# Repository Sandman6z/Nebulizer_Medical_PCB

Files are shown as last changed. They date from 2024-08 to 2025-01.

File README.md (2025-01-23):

## Medical Atomizer on ventilators

- MCU: STM32C031G6U6

- MCU change to: STM32G031G6U6
 ---

## 注意事项
- 由于硅胶垫圈的原因，雾化片震动效果可能不好，更换后，雾化率提升，故降低boost电路电压，R29降为270kΩ
- 经过软件工程师ADC采集数据情况，C18电容NC效果较好
- 保持C20 NC

## 医用雾化器-雾化专用芯片设计注意事项

- 三脚电感值，测试

- 供电输入5V不耐冲击，加TVS等防护
- 高压网络layout和器件封装，参考雾化片手册注意事项
- 雾化片功率检测方式

## 测试数据
### 2024.12.17
- 采样点电流：
  - 有水：133mV
  - 空杯：159mV
  - 无杯：78mV
- MOS电压：
  - 有水：72~90V
  - 空杯：68V
  - 无杯：212V（150V的TVS钳位到160V）

---
---

<!-- 板子背景，更改前的状态，遇到的问题，做的更改，当前设计简述 -->

## 背景信息

- **硬件设计**:
  - 使用Microchip公司的`PIC16F1578-I/SS`微控制器单元(MCU)。
  - 编程环境为`MPLAB X IDE v5.50`，使用`xc8` C语言编译器。
  - 硬件仿真器为`PICKit3`。
  - 通过输出PWM信号驱动MOS管来雾化药物。
  - 与呼吸机通过三根信号线进行通讯，包括使能信号`EN_Fog`、状态反馈信号`NebSt`和设备识别信号`Dev_NC`。

- **软件设计**:
  - 需要实现的功能包括与呼吸机的通信、状态反馈、扫频以确定最佳雾化频率、无水检测等。
  - 雾化器能够通过反馈信号告知呼吸机其工作状态。

## 更改前的状态

- 雾化器能够正常执行基本的雾化操作，但雾化率不理想[需由王工补充]
- 能够与呼吸机进行通信并反馈工作状态，但偶尔无法启动雾化功能
- 已经实现了扫频功能以确定最佳雾化频率，但扫频功能容易误识别

## 遇到的问题

1. **对于PI膜雾化片**:
   - 在剩余约0.5~1ml液体时会误判为无水状态，导致提前停机。
   - 这种误报警现象稳定出现，影响正常使用。

4. **不锈钢雾化片兼容性问题**:
   - 新的不锈钢雾化片与原有雾化片特性不同，需要重新调试扫频、水杯未连接、无水停机策略等来适应新雾化片。

3. **雾化片扫频不准**
   - 当前已经实现了扫频功能，但通过示波器查看扫频波形，若存在多个功率较大的频点时容易误识别，故而不工作在雾化片的最佳频点，需要更精确的电路。

4. **指示灯问题**:
   - 初始化时，工作指示灯的亮度不足，可能是软件控制的问题。

5. **LED状态问题**:
   - 当使能信号被取消后，LED会锁定在红色状态，无法回到初始化状态，除非重新启动雾化器。

这些问题需要进一步的软件优化和调试来解决，以确保雾化器的稳定运行和提高用户体验。

## 问题更改及改进

1. MCU
   - 原MCU为microchip的PIC16F1578-I/SS，IDE使用MPLAB X IDE，配置复杂，且软件通用性差，与公司生态不一致
   - 考虑到性能、价格、封装、生态等因素，将microchip MCU换成ST的STM32C031G6U6，价格近似，性能有质的提升，且外设满足所有功能，精度更高，封装尺寸小，更便于布局。与原厂FAE和各经销商确认过，供货长期且稳定，若量大价格可以更低
   - STM32C0系列与STM32G系列多种型号封装互相通用，后期若需要修改，也有更多选择，而无需修改PCB
   - 使用STM32CubeMX，使用图形化配置 + HAL库的方式，实现快速开发，满足易维护的要求

2. MOSFET
   - 原雾化电路驱动的LC电路可达到100V以上，但原NMOS耐压值不足，本次选择onsemi(安森美)家的FDN86246，耐压可达150V，Id 1.6A，均满足设计需求且余量充足
   - 封装更小，节省紧张的板空间

3. 扫频功能
   - 增加雾化驱动电路的电压和电流检测电路
   - 电压检测通过分压方式；电流检测通过检流电阻和运放电路的方式
   - 相较原简易电阻分压测电流方式，精度更高，且layout采用差分走线，避免layout造成的采样不准确的问题
   - 将电压和电流检测电路结合，配合软件逻辑，实现扫频功能。

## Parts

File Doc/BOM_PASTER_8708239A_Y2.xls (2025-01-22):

型号 | 封装 | 位号 | 元件编号
15nF±5%50VX7R | C0402 | C18,C21 | C114405
STM32G031G6U6 | QFN50P400X400X60-28N-D | U4 | C432210
510Ω±1%62.5mW | R0402 | R14,R15,R3,R4,R5,R6,R7,R8,R9 | C25123
30Ω±1%62.5mW | R0402 | R16 | C514796
1.25T-6P-WT | WAFER_1.25MMX6P_180 | J2 | C97377
1.25T-3P-WT | WAFER_1.25MMX3P_180 | J1 | C707315
100pF±5%100V | C0603 | C4 | C107033
1uF±10%25VX5R | C0402 | C1,C2 | C52923
SS24 | SMA-403D | SD1 | C50645
AO3410 | SOT23-3 | Q2 | C7524909
10uH/2.5A | SP0502 | L3 | C65664
1kΩ±0.1%62.5mW | R0402 | R33,R37 | C852624
330Ω±1%62.5mW | R0402 | R21,R32,R34 | C427237
220Ohm@100MHz | 0402-B | B1,B2,B4,B5,B6 | C85813
1K±25%@100MHz | 0805-B | B10,B3,B7 | C85835
10KΩ±1%62.5mW | R0402 | R28,R1,R13,R27 | C850723
4.7kΩ±1%62.5mW | R0402 | R11 | C400631
ME6211C33M5G-N | SOT95P270X145-5N | U2 | C82942
100nF±10%50VX7R | C0402 | C13 | C307331
0Ω±1%100mW | R0603 | R10,R30 | C21189
LED_BLUE | LED0603 | LED8,LED9,LED1,LED3,LED4,LED5,LED2 | C965807
10kΩ±1%62.5mW | R0402 | R20,R12,R25 | C25744
4.7kΩ±0.1%62.5mW | R0402 | R38,R35 | C728561
22uF±20%25V | C0805 | C10,C12,C8,C9,C11 | C45783
1Ω±1%500mW±100ppm/℃ | R1206 | R31 | C1882606
390kΩ±1%100mW | R0603 | R24,R26 | C23150
HSS1N20 | SOT95P237X122-3N | Q1 | C845589
TLV9051IDBVR | SOT23-5 | U1 | C1849429
47Ω±1%62.5mW | R0402 | R17,R19 | C427232
100nF±10%50VX7R | C0402 | C14,C15,C6,C16,C19 | C1525
AO3401 | SOT23 | Q3 | C727156
LED_GREEN | LED0603 | LED7 | C7371905
PESD5V2S2UT | SOT23 | ESD1,ESD2,ESD3 | C2827690
4.7uF±10%10VX5R | C0402 | C5 | C368809
LED_RED | LED0603 | LED6 | C965799
470uH±10%260mA | SP0502 | L2 | C167984
BZG03C150-M3-08 | DIOM5226X230N | TVS1 | C2761030
MT3608 | SOT95P280X110-6N | U3 | C84817
280kΩ±1%62.5mW | R0402 | R29 | C364982
NC | C0402 | ES10,ES11,ES9 | NC
22uH@100kHz/50V1812 | LINEFILTER | L1 | NC
NC | C0402 | C20 | NC
NC | JST_PH2.00-5 | J3 | NC

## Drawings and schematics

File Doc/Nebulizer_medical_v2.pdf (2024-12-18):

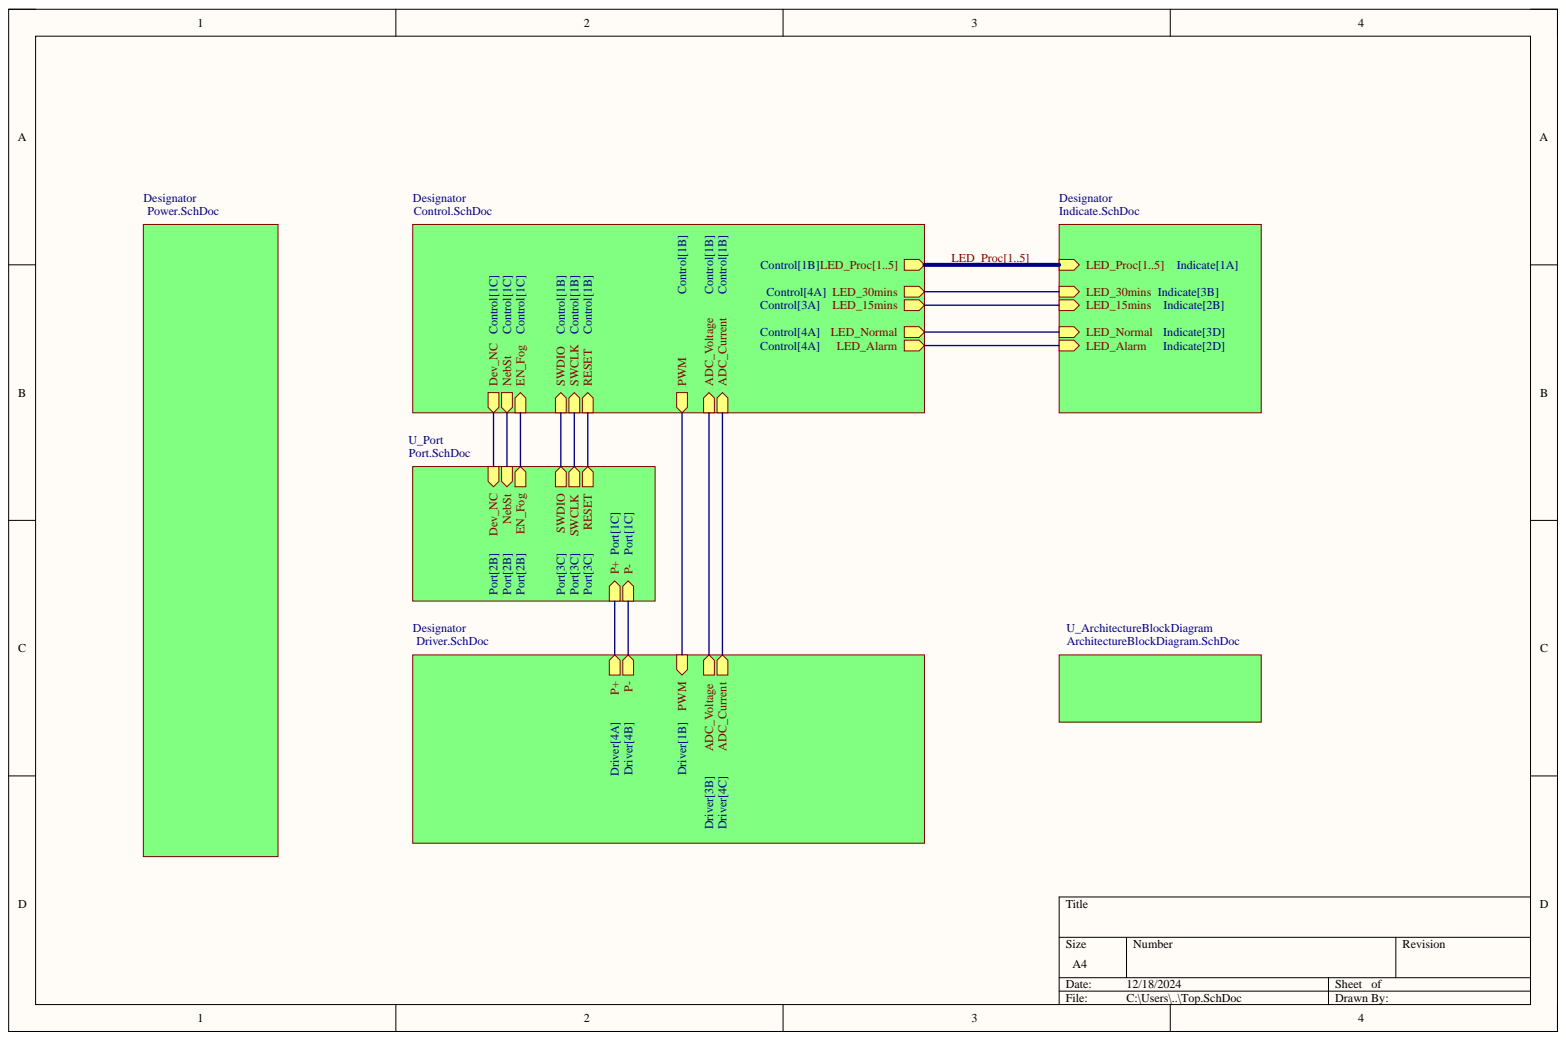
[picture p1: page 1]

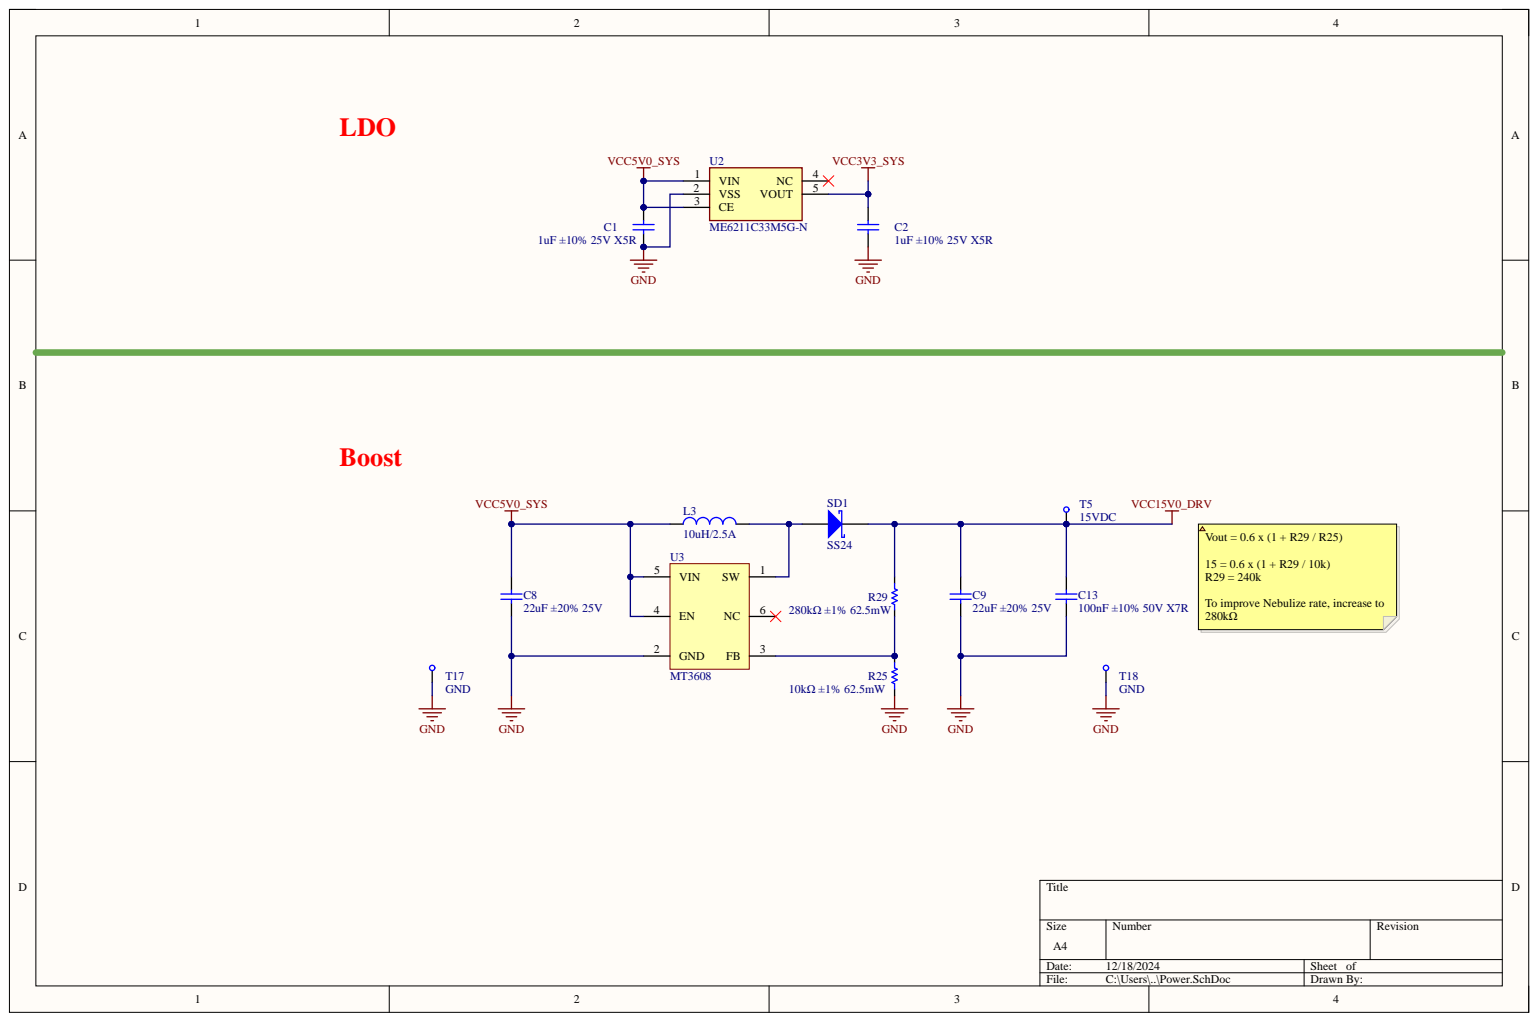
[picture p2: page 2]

To improve Nebulize rate, increase to

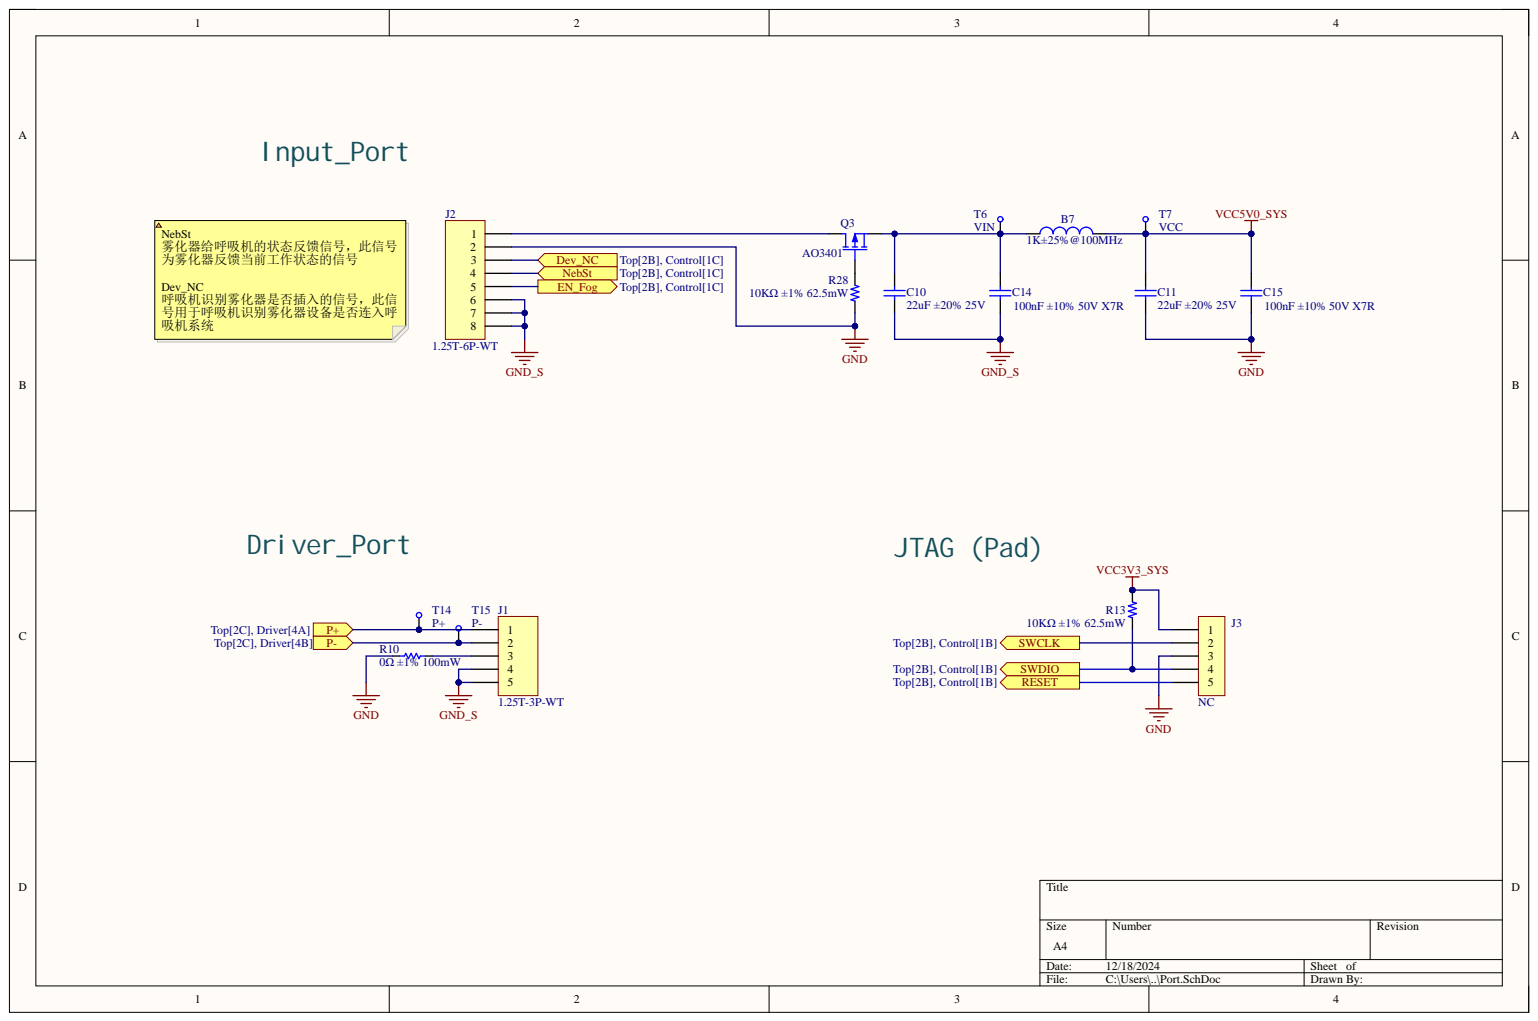
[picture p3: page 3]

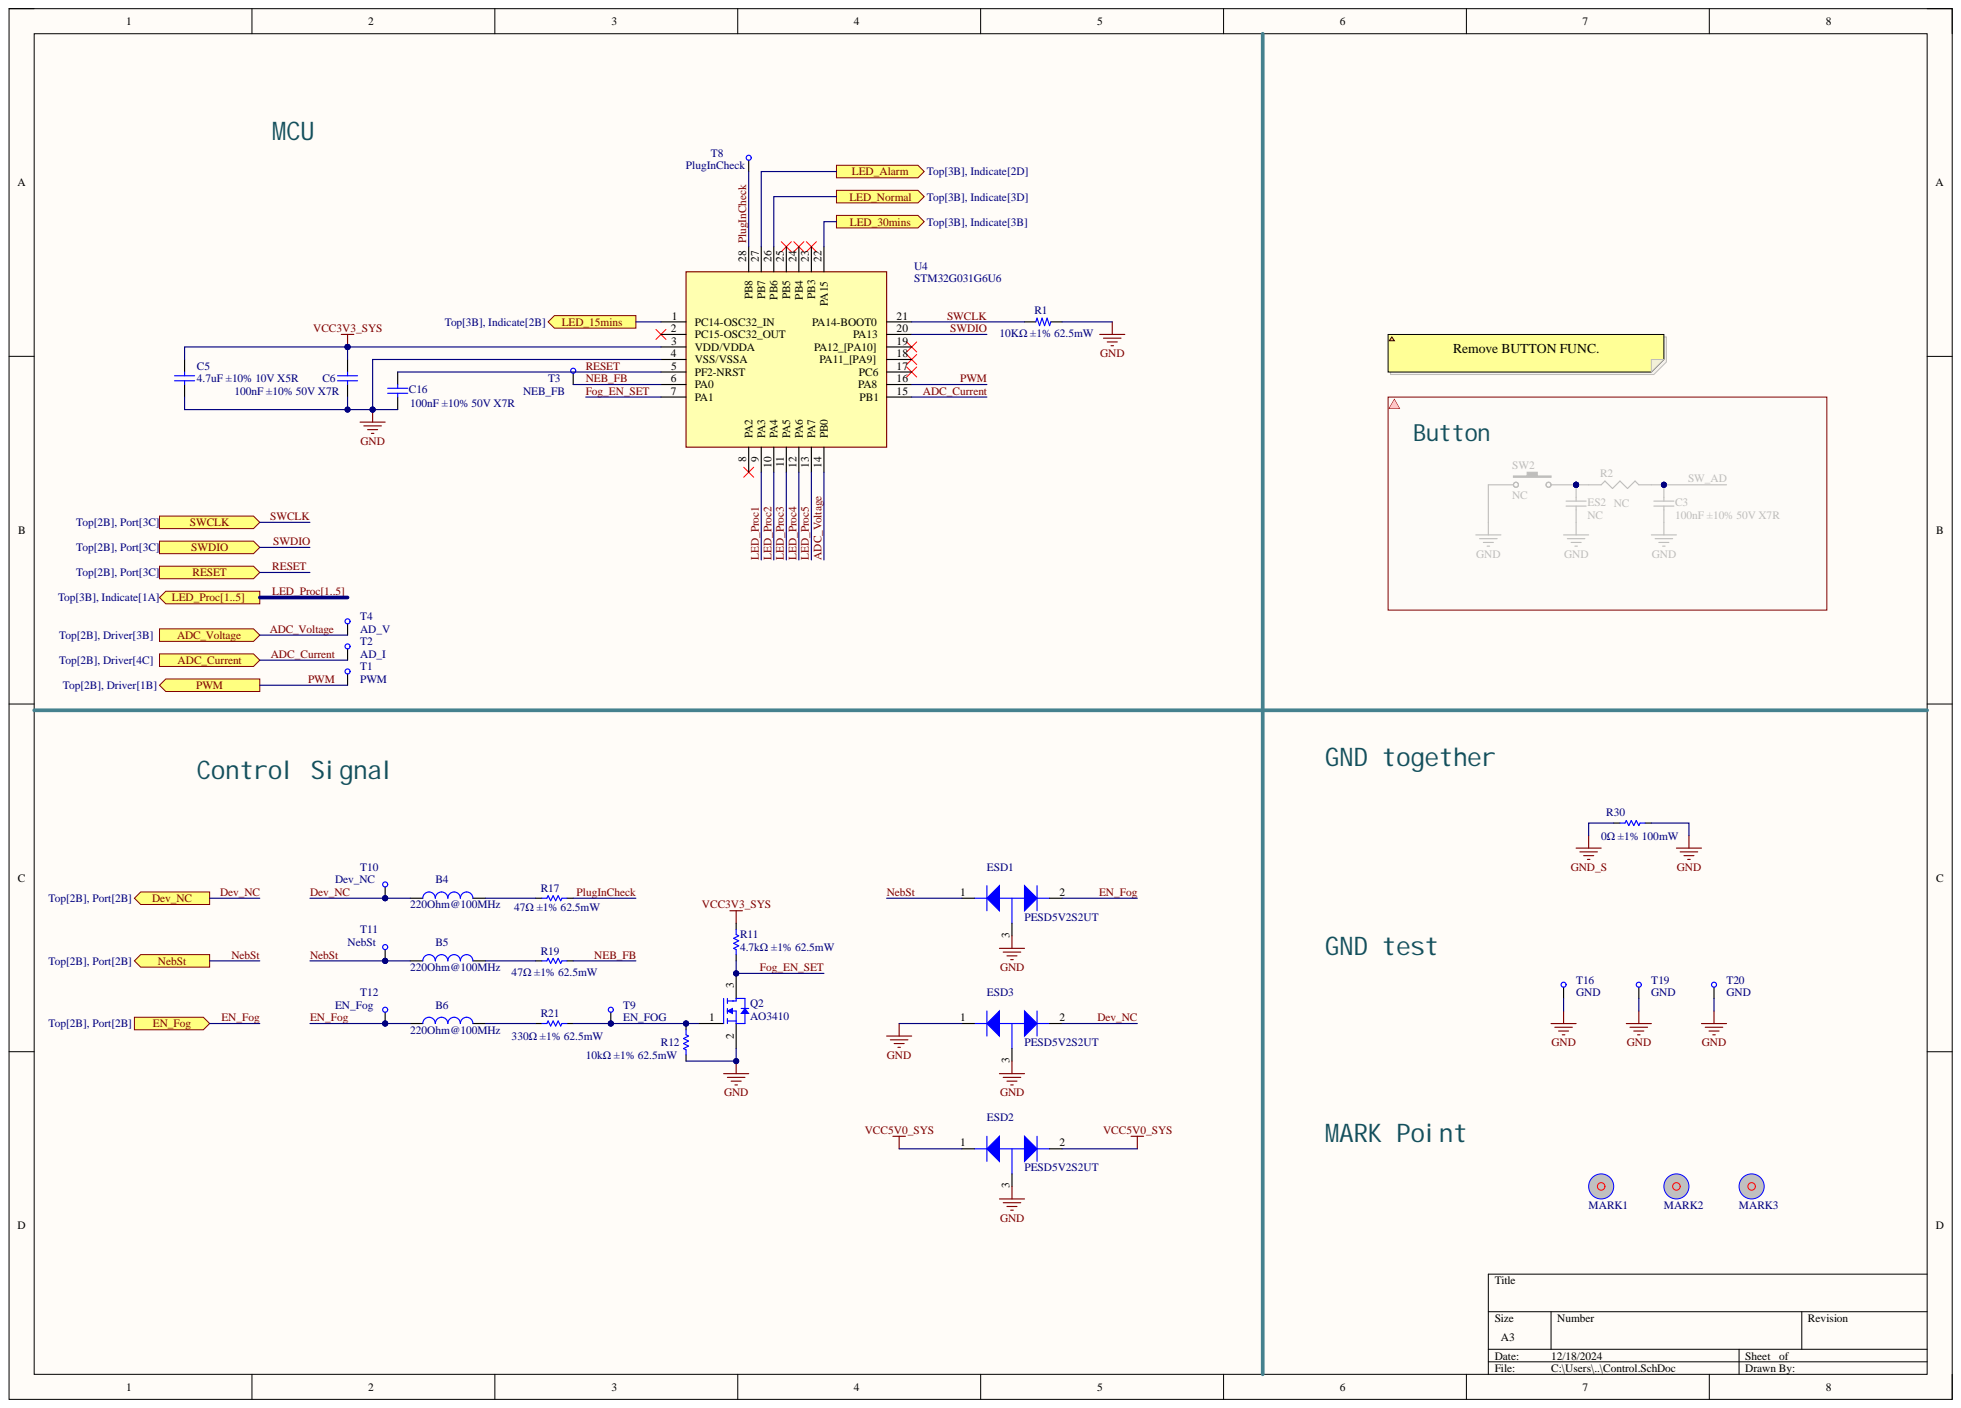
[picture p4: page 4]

VSS/VSSA 4

RESET | PF2-NRST 5

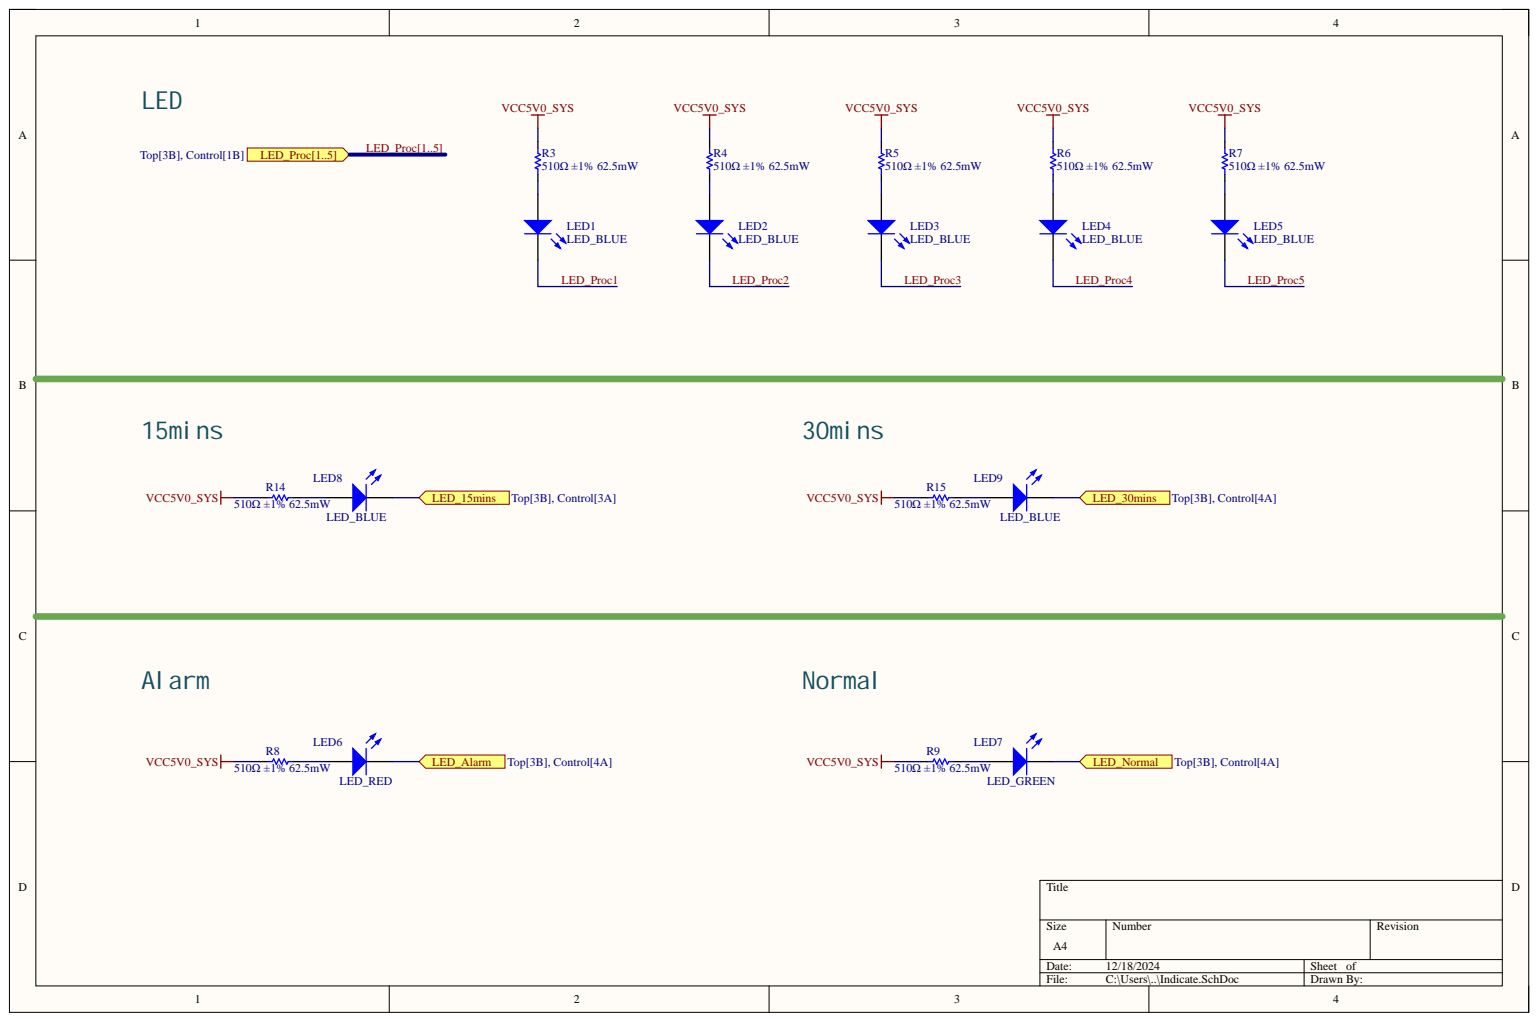
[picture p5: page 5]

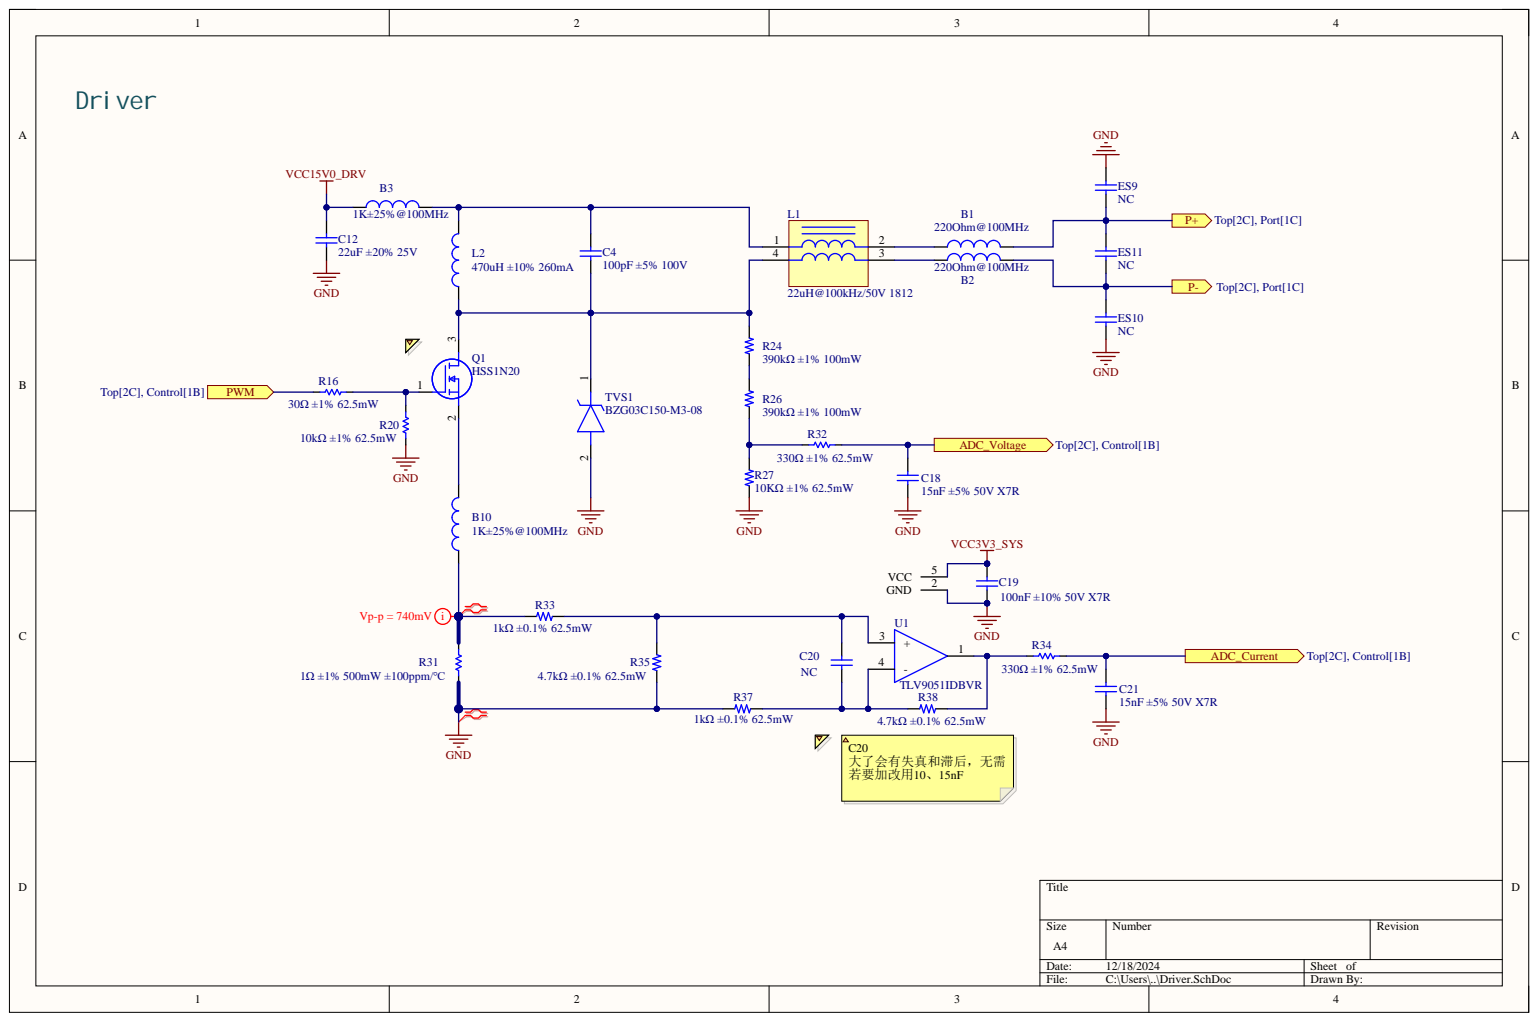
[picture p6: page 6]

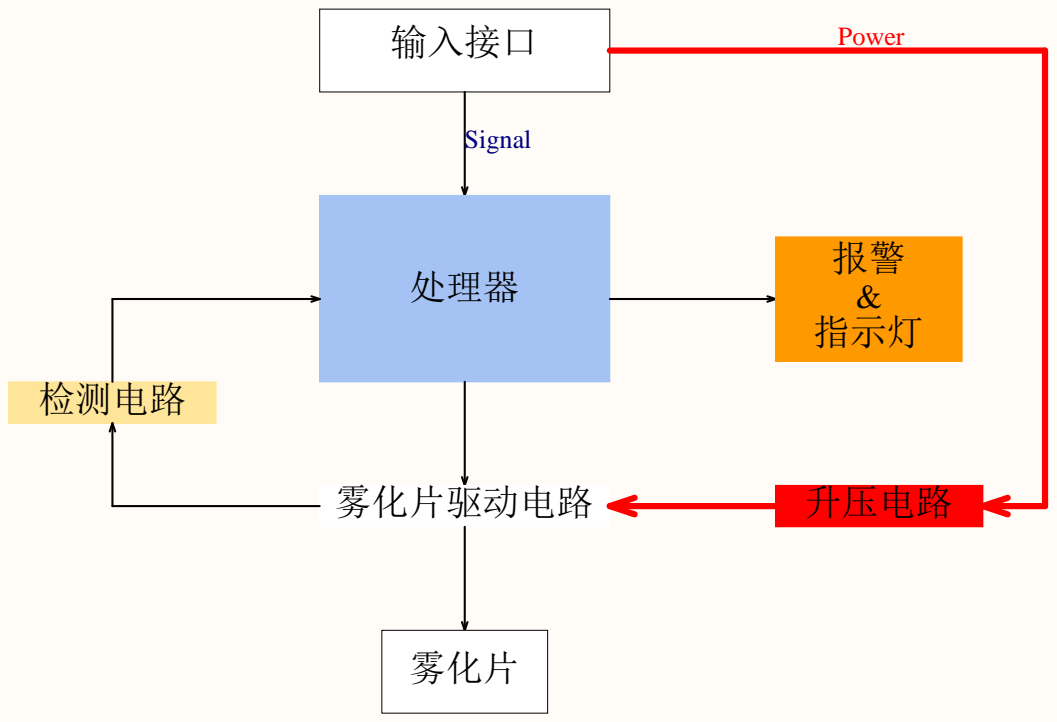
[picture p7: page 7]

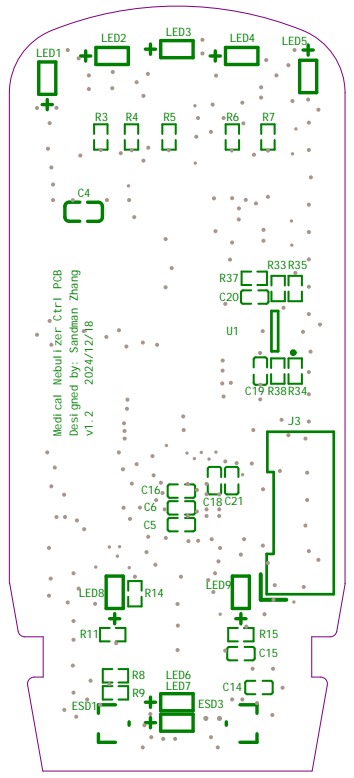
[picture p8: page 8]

Medical Nebulizer Ctrl PCB

Designed by: Sandman Zhang

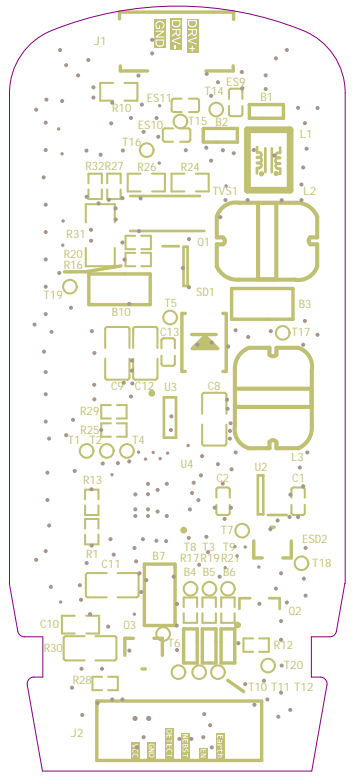
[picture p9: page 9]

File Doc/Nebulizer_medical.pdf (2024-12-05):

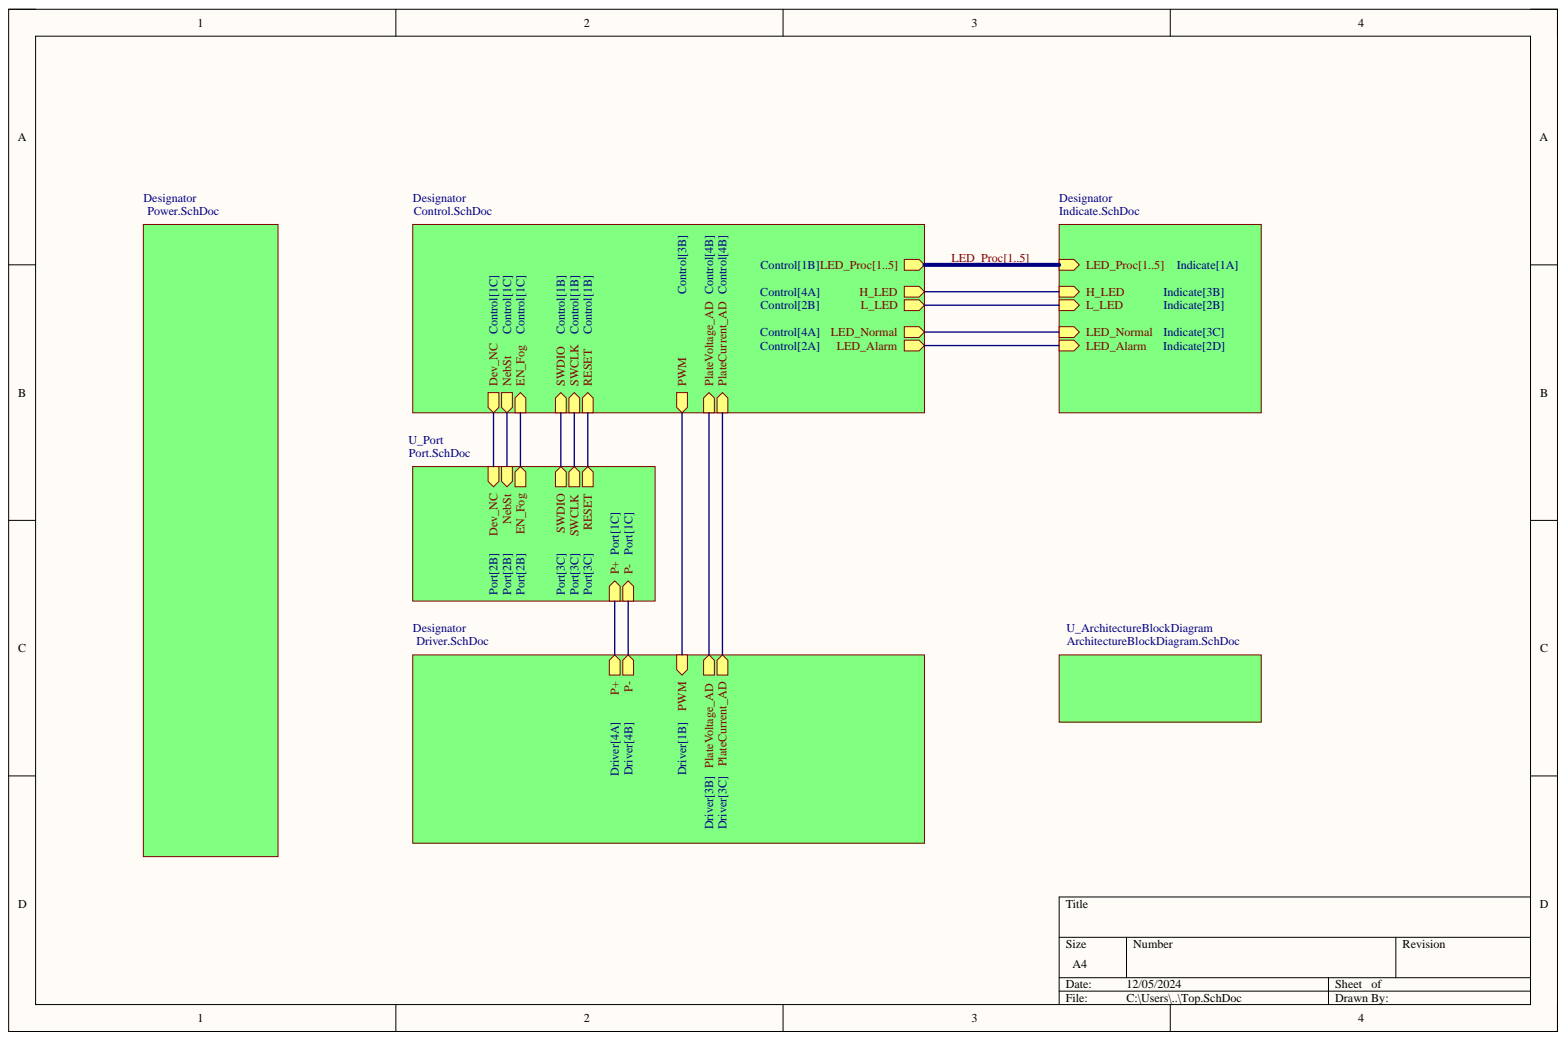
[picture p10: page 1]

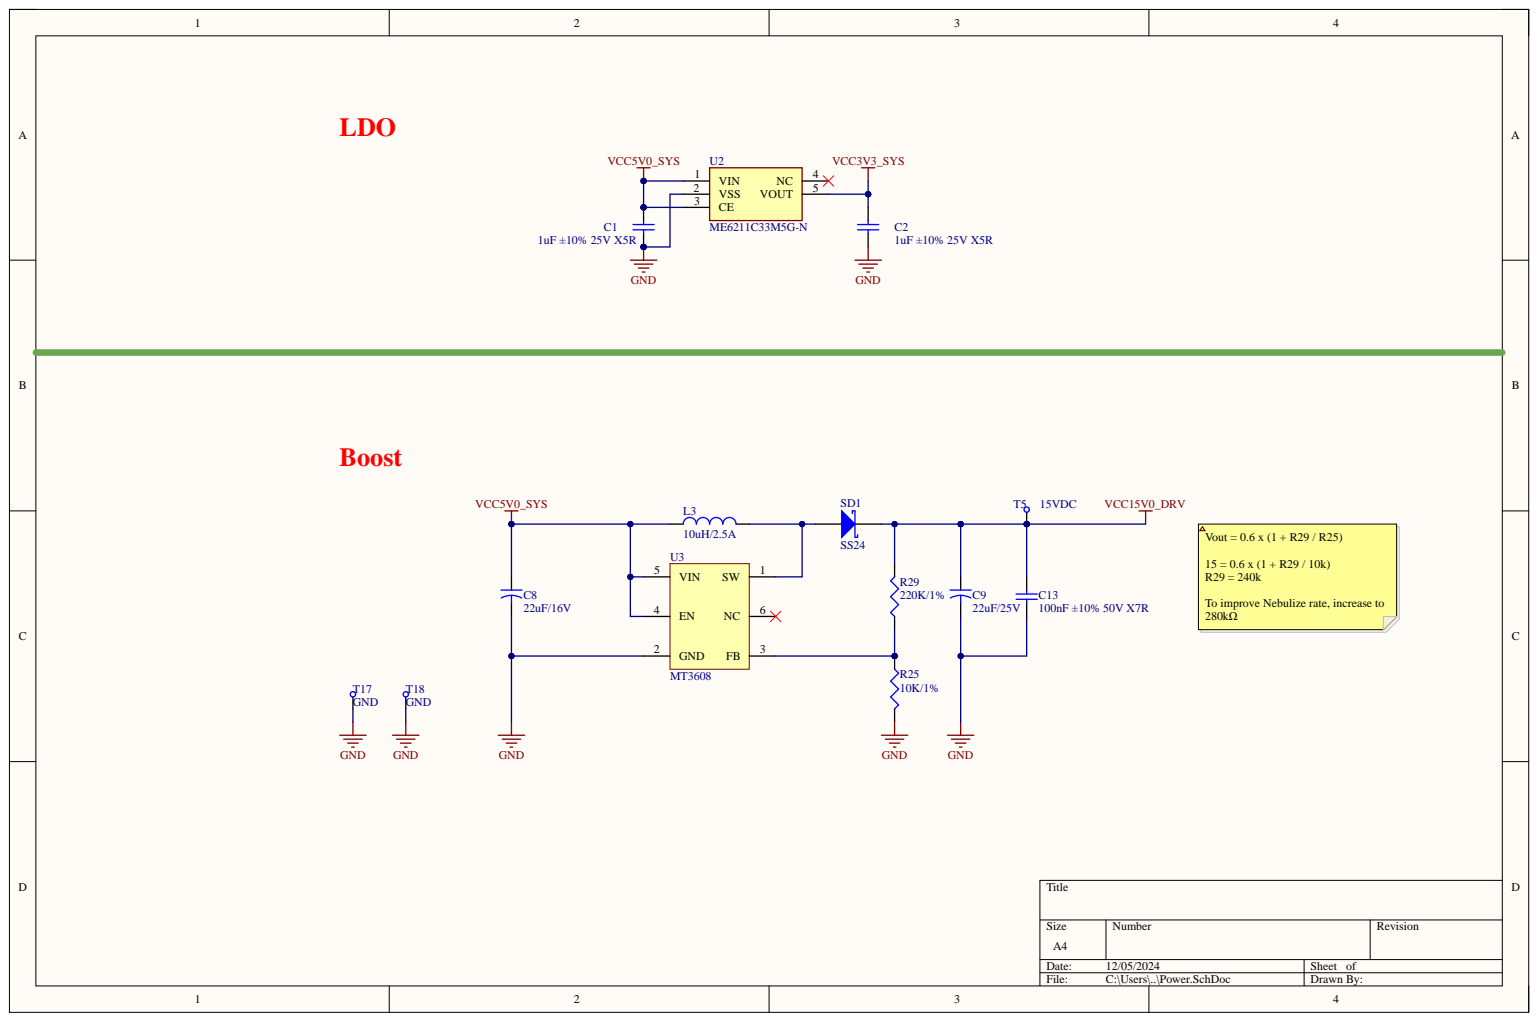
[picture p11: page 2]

To improve Nebulize rate, increase to

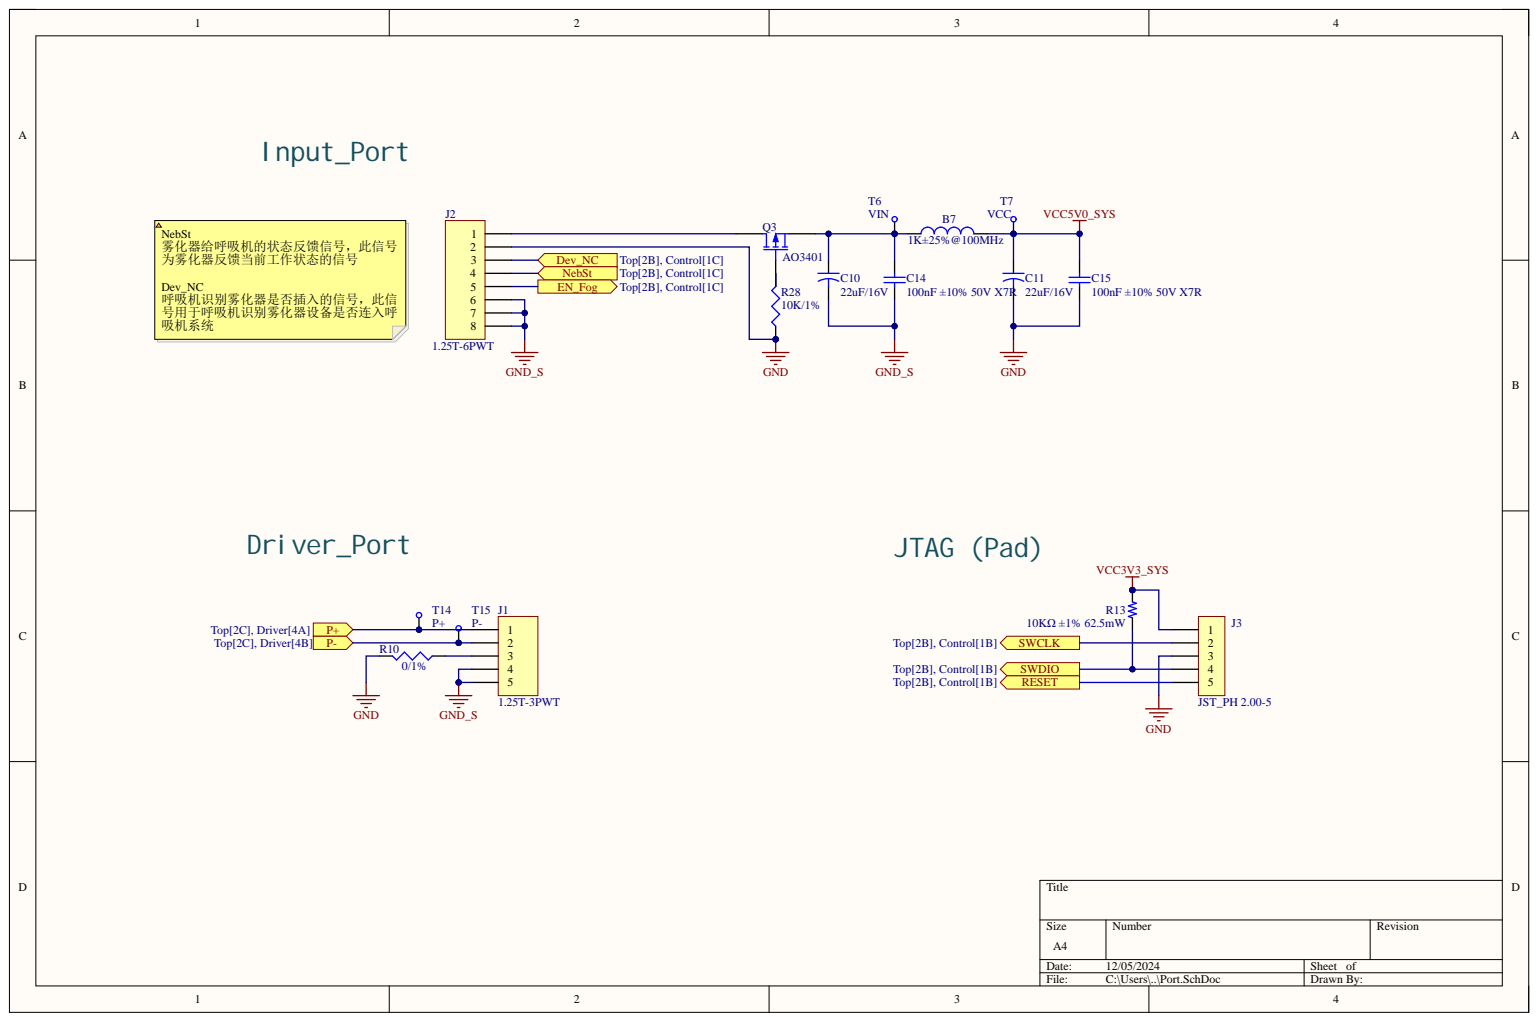
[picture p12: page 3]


VSS/VSSA 4

RESET | PF2-NRST 5

PWM | | CT_AD







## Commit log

2024-07-23 original files
    [Atomizer_medical_V1_4.PCBDOC, Atomizer_medical_V1_4.PrjPcb, Atomizer_medical_V1_4.SchDoc, BOM_Atomizer_medical_V1_3_20211009 - 副本.xlsx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]
2024-07-23 rename files & update PCB from sch
    [Atomizer_medical.PCBDOC, Atomizer_medical.PrjPcb, Atomizer_medical.SchDoc]
2024-07-23 add new MCU & add .gitignore
    [Atomizer_medical.PCBDOC, Atomizer_medical.SchDoc]
2024-07-23 add MCU
    [Atomizer_medical.PCBDOC, Atomizer_medical.SchDoc]
2024-08-01 doing pinning
    [Atomizer_medical.PCBDOC, Atomizer_medical.PrjPcb, Atomizer_medical.SchDoc, Atomizer_medical_V1_4.PCBDOC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]
2024-08-02 Finish adjust MCU pin
    [Atomizer_medical.PCBDOC, Atomizer_medical.SchDoc]
2024-08-02 ready change name from atomizer to nebulizer.
    [Atomizer_medical.PrjPcb]
2024-08-02 change name from Atomizer to Nebulizer.
    [Atomizer_medical.SchDoc, Nebulizer_medical.PrjPcb]
2024-08-02 rename all files & seperate schdoc
    [Atomizer_medical.PCBDOC, Indicate.SchDoc, Nebulizer_medical.PcbDoc, Nebulizer_medical.PrjPcb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]
2024-08-05 seperate schdoc for more part, change some package
    [Driver.SchDoc, Nebulizer_medical.PcbDoc, Nebulizer_medical.PcbLib, Nebulizer_medical.PrjPcb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]
2024-08-05 change Drive SchDoc
    [Driver.SchDoc, Nebulizer_medical.PcbDoc, Nebulizer_medical.PrjPcb, Nebulizer_medical.SchDoc]
2024-08-06 adjust circuit
    [Driver.SchDoc, Nebulizer_medical.PcbDoc, Nebulizer_medical.PrjPcb, Nebulizer_medical.SchDoc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]
2024-08-12 adjust layout
    [Driver.SchDoc, Nebulizer_medical.PcbDoc]
2024-08-20 layouting... need to refer original version
    [Nebulizer_medical.PcbDoc, Nebulizer_medical.SchDoc, Power.SchDoc]
2024-08-20 first finish layout
    [Nebulizer_medical.PcbDoc, Nebulizer_medical.PcbLib, Nebulizer_medical.PrjPcb, Nebulizer_medical.SchDoc]
2024-08-21 change Current capture layout had been changed to differential by Hening
    [Nebulizer_medical.PcbDoc]
2024-08-21 FINISH LAYOUT
    [Control.SchDoc, Indicate.SchDoc, Nebulizer_medical.PrjPcb, Nebulizer_medical.SchDoc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]
2024-08-21 BOM changed
    [Atomizer_medical_V1_4.PCBDOC, BOM_Atomizer_medical_V1_3_20211009 - 副本.xlsx, BOM_Atomizer_medical_V1_3_20211009.xlsx, Nebulizer_medical-立创商城报价.xlsx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]
2024-08-22 fix BOM Q1 model wrong
    [Nebulizer_medical-立创商城报价.xlsx]
2024-08-23 change current detect differencial ploygen layout
2024-09-03 fix solder layers not have all components bug
2024-09-06 BOM have Component encapsulation problem, change with links on SZLCSC
    [452007132 医用雾化器控制板 BOM_Q.xlsx]
2024-09-15 add top struct, use label instead of offsheet symbol
    [Control.SchDoc, Driver.SchDoc, Indicate.SchDoc, Nebulizer_medical.PrjPcb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]
2024-09-17 add top files, and change structure to multiple and entire.
    [Control.SchDoc, Driver.SchDoc, Indicate.SchDoc, Top.SchDoc]
2024-09-26 add struct sheet and adjust others
    [ArchitectureBlockDiagram.SchDoc, Control.SchDoc, Driver.SchDoc, Nebulizer_medical.PrjPcb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]
2024-09-29 add port sheet and let all ports from other sheets into it
    [Control.SchDoc, Driver.SchDoc, Nebulizer_medical.PrjPcb, Port.SchDoc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]
2024-09-29 Fix Voltage detect resistor 0402 to 0603
    [Driver.SchDoc]
2024-10-08 1. Annoteted the op amp differential sampling circuit;
    2. Fix 0402 power parameter from 67.5mW to 100mW;
    3. Updated the PCB.
    [Control.SchDoc, Driver.SchDoc]
2024-10-11 1. NMOS WRONGgit add .! 2. change all port I/O direction
    [Control.SchDoc, Driver.SchDoc, Indicate.SchDoc, Port.SchDoc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]
2024-10-25 adjust Driver.sheet some component value. Opinions from Sunke
    [Driver.SchDoc]
2024-10-31 Remark Omp. Voltage need to change higher.
    [Driver.SchDoc]
2024-11-08 change FB up Resistor value
    [Power.SchDoc]
2024-11-11 change MOS alternative type
    [Driver.SchDoc]
2024-11-15 add some none 3D body
    [Nebulizer_medical.PcbLib, Nebulizer_medical.PrjPcb]
2024-11-15 add IO port 3D body
    [Nebulizer_medical.PcbLib]
2024-11-18 annotation 1Ω Res. use check-current-Res.
    [Driver.SchDoc]
2024-11-20 add some test param
    [Control.SchDoc, Driver.SchDoc, Indicate.SchDoc]
2024-12-05 1. Only change schdoc; 2. Adjust schdoc all part layout & position, make it more orderly
    [Control.SchDoc, Driver.SchDoc, Indicate.SchDoc, Port.SchDoc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]
2024-12-05 1. adjust layout after remove no useful Cap.; 2. generate pdf for fast check; 3. move proj. design docs to outside folders.
    [Indicate.SchDoc, Nebulizer_medical.PrjPcb]
2024-12-06 1. format schdoc; 2. update README
    [Driver.SchDoc, Port.SchDoc]
2024-12-09 [Significant Changes] 1. Change some pin IO; 2. change & add some IO name; 3. change Driver part; 4. Update PCB but not adjust.
    [Control.SchDoc, Driver.SchDoc, Indicate.SchDoc, Port.SchDoc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]
2024-12-10 1. change component paras.; 2. re-layouting
    [Driver.SchDoc]
2024-12-12 change layout of capture RES
    [Control.SchDoc, Nebulizer_medical.PrjPcb]
2024-12-13 change ADC current capture part
    [Control.SchDoc, Driver.SchDoc]
2024-12-17 almost finish layout, left replace MCU and adjust silk.
    [Driver.SchDoc]
2024-12-17 1. change MARK posi. & add one; 2. finish adjust silk
    [Control.SchDoc]
2024-12-17 1. clear inner ploygen of current capture part from resistor; 2. add Via to MCU GND; 3. adjust boost Output capacitor close to Pin 2 of chip
2024-12-17 change MCU from C031 to G031
    [Control.SchDoc]
2024-12-17 change Op Amps type to TLV9051IDBVR
    [Driver.SchDoc]
2024-12-18 1. change MCU port; 2. change TVS name; 3. adjust PCB layout
    [Control.SchDoc, Driver.SchDoc, Nebulizer_medical.PrjPcb]
2024-12-18 1. change all component commit&description for BOM; 2. generate bomdoc; 3. update PCB; 4. delete annotion & pcblib files“
    [Control.SchDoc, Driver.SchDoc, Indicate.SchDoc, Nebulizer_medical.PcbLib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]
2024-12-18 generate lastest pdf
    [Nebulizer_medical.PrjPcb]
2024-12-24 remove created pcblib
    [Nebulizer_medical.PrjPcb]
2025-01-21 no bug; add BOM.xls
    [BOM_PASTER_8708239A_Y2.xls, Driver.SchDoc]
2025-01-22 change BOOST FB resistor R29:280k -> 270k. See README for details
    [BOM_PASTER_8708239A_Y2.xls]
